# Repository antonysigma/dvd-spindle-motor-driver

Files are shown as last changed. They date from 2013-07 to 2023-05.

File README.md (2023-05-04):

# Spinning flow-cell controller with conventional DVD/BD drives

The custom PID controller board to maintain the rotation speed of the DVD/BD
drive at a user-provided RPM value.

Note: This project is inspired by the blog post
http://akashkumar4u.blogspot.hk/2013/05/cddvd-motor-driver-hack-to-run-its-own.html

Technical specifications:

* Input power: 5VDC, 200mA;

* Output: torque control signal for the DVD spindle motor driver IC, [Rohm BD7998EFS](datasheet/bd7956fs.djvu).

* RPM speed sensing: rotary encoder pulse signal, converted from the built-in hall sensor of the DVD drive.

* Display: kilo-RPM value on the 7-segment LED numerical display;

* MCU Programming interface: SPI bus to program the ATTiny MCU.

* Set point control: Manual adjustment knobs; one for coarse adjustment (+/- 1
  kilo-RPM); one for fine adjustment (+/- 50 RPM).

## Why I made my own board

The board is part of the rotational digital histology imaging system: to study how one can rapidly image a custom Petri dish with adherent mammalian cells. The disk/dish is scanned with a one-dimensional image sensor (at 100 MHz line rate) following a outward spiral trajectory, so it is absolutely necessary to control the RPM precisely for image registration.

Reference: Anson H. L. Tang, P. Yeung, Godfrey C. F. Chan, Barbara P. Chan, Kenneth K. Y. Wong, and Kevin K. Tsia, “Time-stretch microscopy on a DVD for high-throughput imaging cell-based assay,” Biomed. Opt. Express 8, 640–652 (2017). https://doi.org/10.1364/BOE.8.000640

The schematic is eventually re-designed to synchronize the RPM with the x-axis linear stage.

## Preview

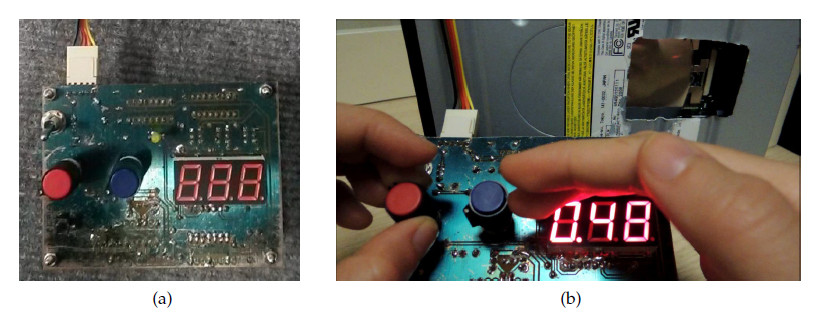
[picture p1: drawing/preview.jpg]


## Schematics

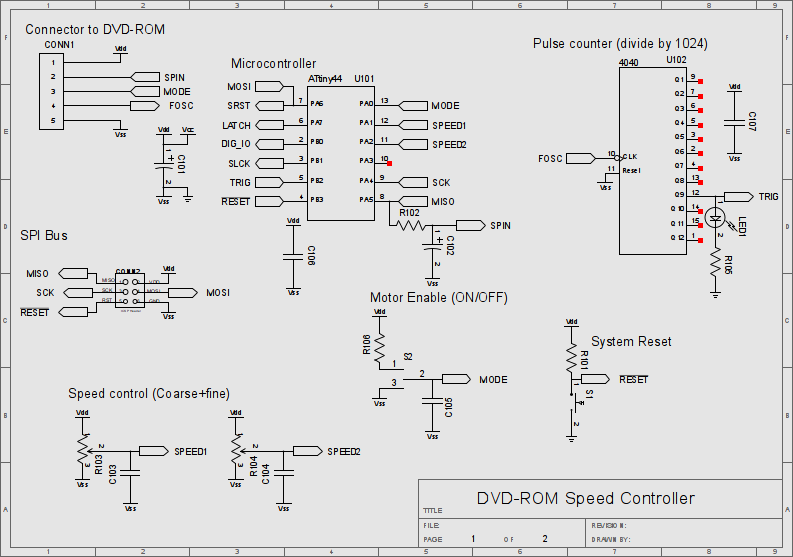
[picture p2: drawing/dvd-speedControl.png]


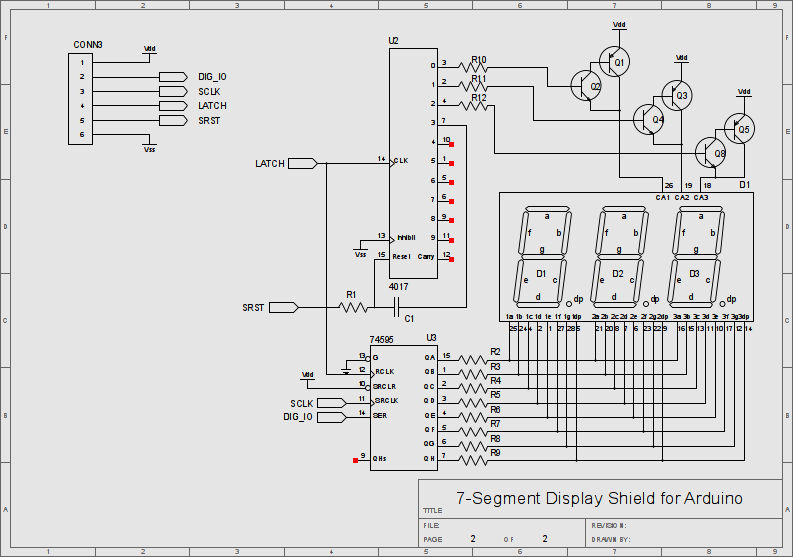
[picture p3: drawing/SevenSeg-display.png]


## Design intent

The overarching goal, at the time, was to justify the investment of custom control circuit in an optics research lab. With minimal budget, I wish to prove that:

* it is intuitive enough to reverse-engineer a conventional DVD drive for manual RPM control;

* advanced control logic, e.g. lead-lag compensation, can be programmed with MCUs; no hardwired analog OpAmp circuit required.

* the RPM control board and the DVD drive can be quickly integrated into the high-speed microscopy system (at 100 image line scan rate) without impacting research timeline.

... so I can justify more inventment on a professionally made driver board for the research, like what [Ultima Genomics did with their spinning flowcells](https://www.biorxiv.org/content/10.1101/2022.05.29.493900v1.full).

**Understanding the DVD motor spindle driver IC** The DVD drive is dissembled to
inspect spindle motor driver IC (Fig. 1a) on the control board. The
corresponding datasheet is sought from the Internet to locate the essential pin
to interface with the motor control functions (Fig. 1b). Specifically, pin 35,34
toggles between spindle motor enable and DVD tray enable; pin 26 controls the
spindle motor torque; pin 43 relays the speed information back to the
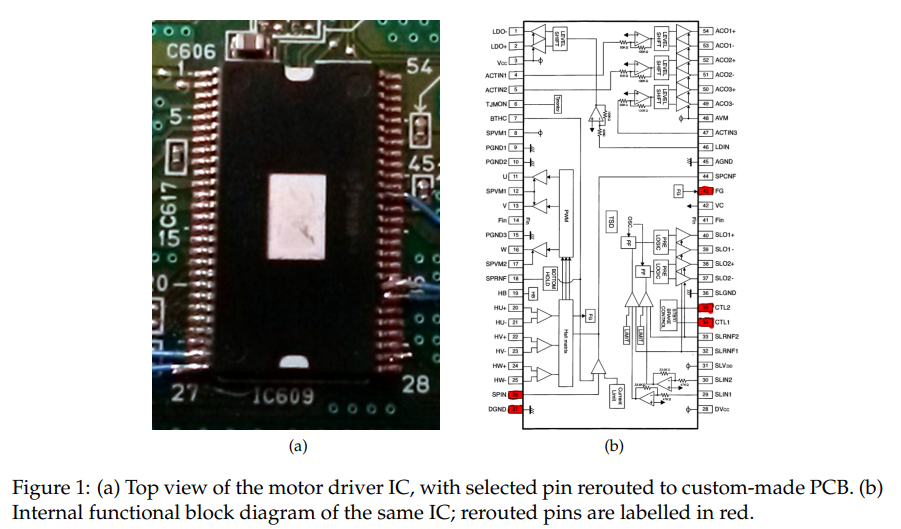
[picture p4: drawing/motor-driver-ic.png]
microcontroller (Fig. 1). 

**Developing the feedback control theory**

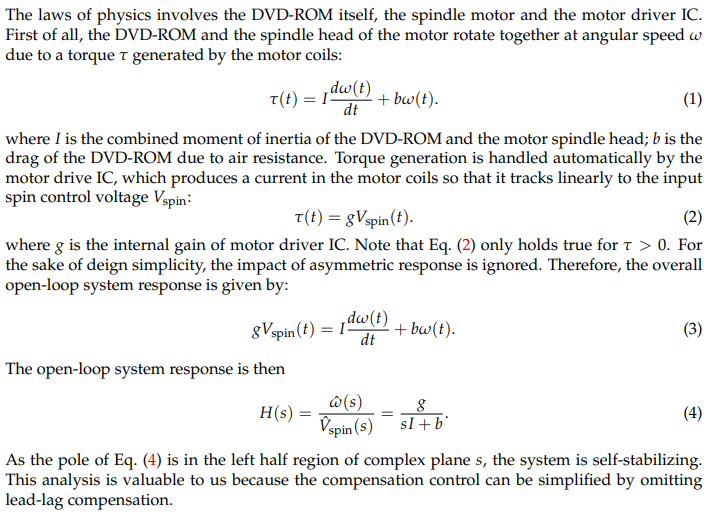
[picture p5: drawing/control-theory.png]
control theory

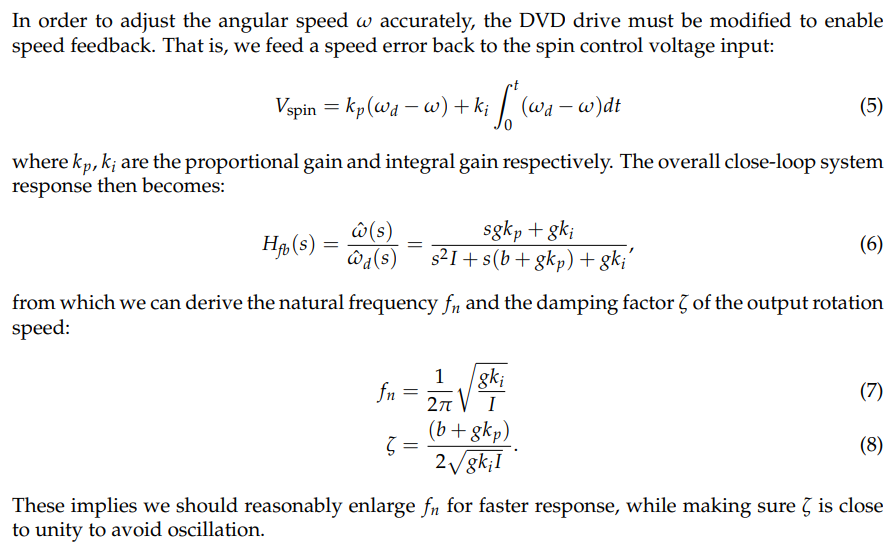
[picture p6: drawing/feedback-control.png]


**Decoding the rotary encoder signal**

The same DVD spindle motor IC also decodes the built in Hall sensor to return
the 3 phase quadrature signal at TTL. For the quick prototyping purpose, we do
not need to tell the absolute position or the spin direction of the disk, so we
only pick one signal out of the 3 phase bus to measure speed.

We offload pulse conuting logic to an external IC (74HC4040) to reduce the pulse
rate by 1024 times. Otherwise, the MCU running at 8MHz will be overwhelmed by
the edge interrupt. The RPM measurement is implemented in the MCU, we the time
interval between adjacent edge interrupt is estimated from the 8MHz MCU clock.

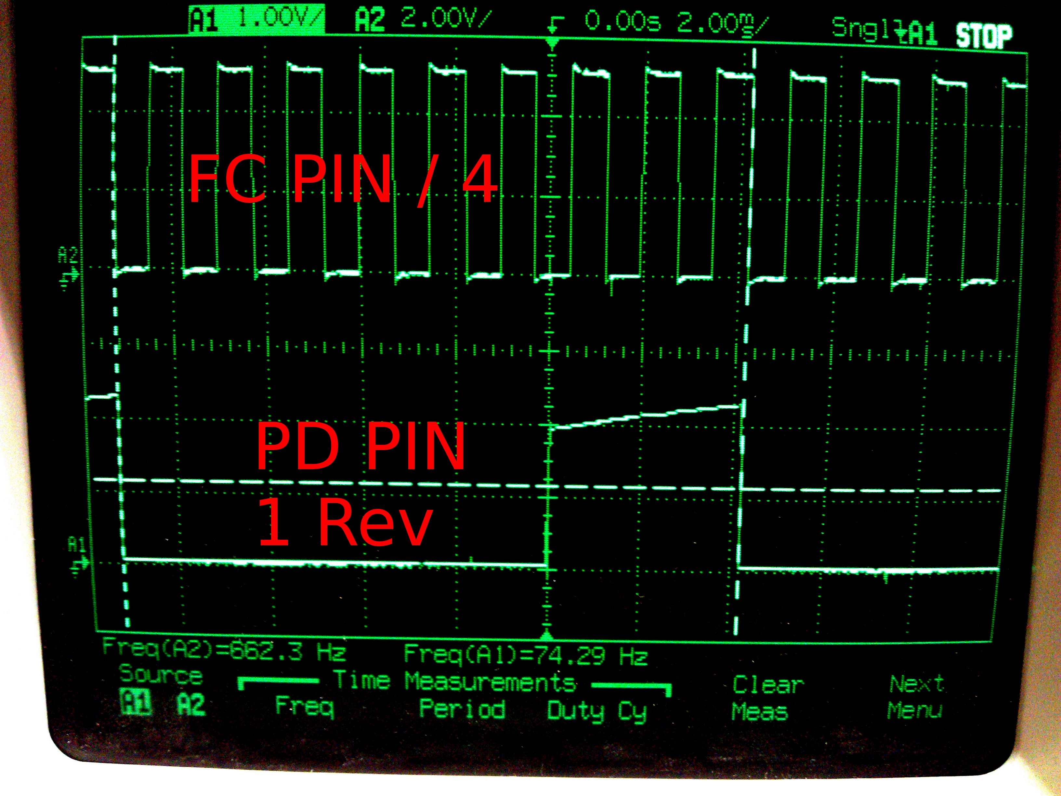
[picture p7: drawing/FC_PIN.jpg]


## PCB routing

The board was designed at the time when solder paste and cheap PCB fabhouse were cost prohibitive. We developed the photo-resist mask, and etch the PCB in house.
Through hole component were the only options. To create throughhole vias, a solid core copper at 22 AWG were inserted and buried with solder.

If I were to route the PCB again, I would have used SMT components to shrink the board down.

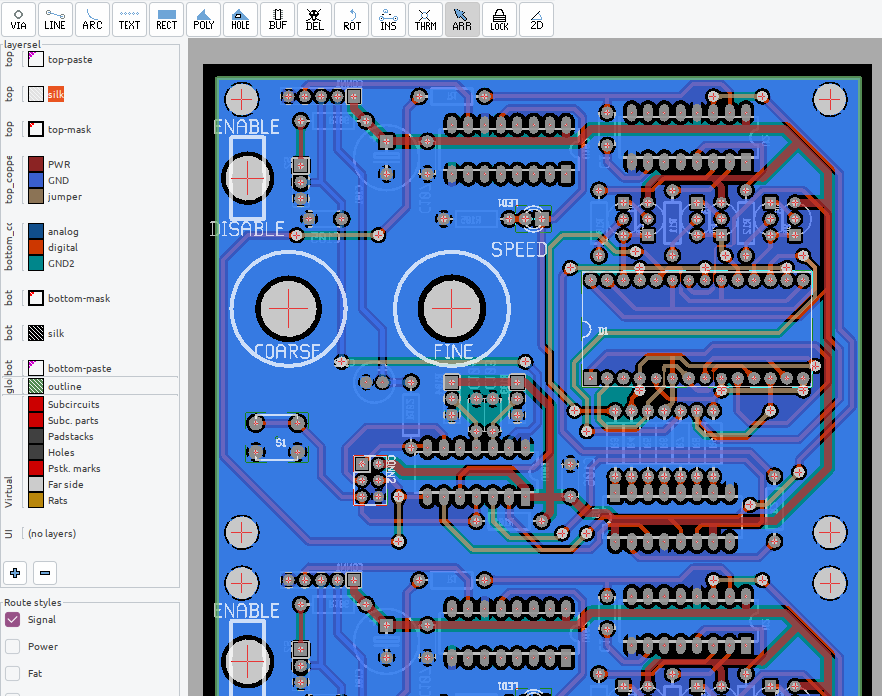
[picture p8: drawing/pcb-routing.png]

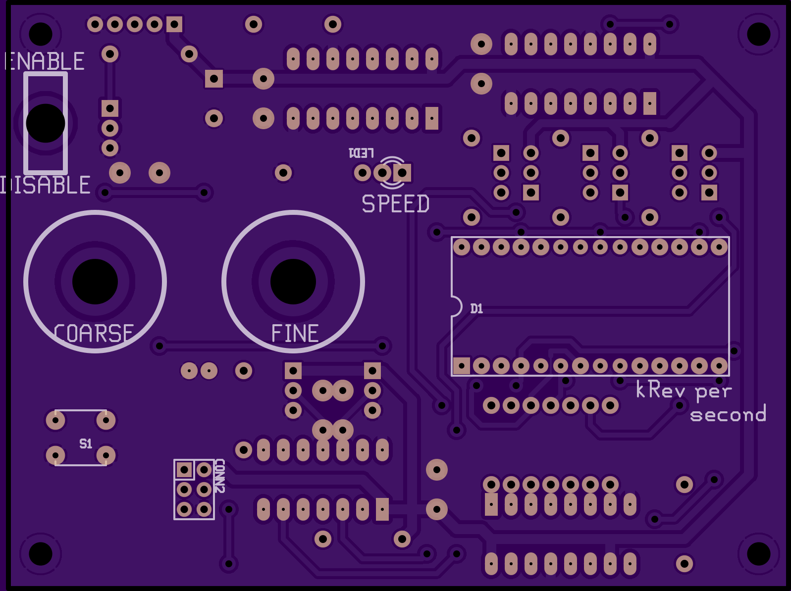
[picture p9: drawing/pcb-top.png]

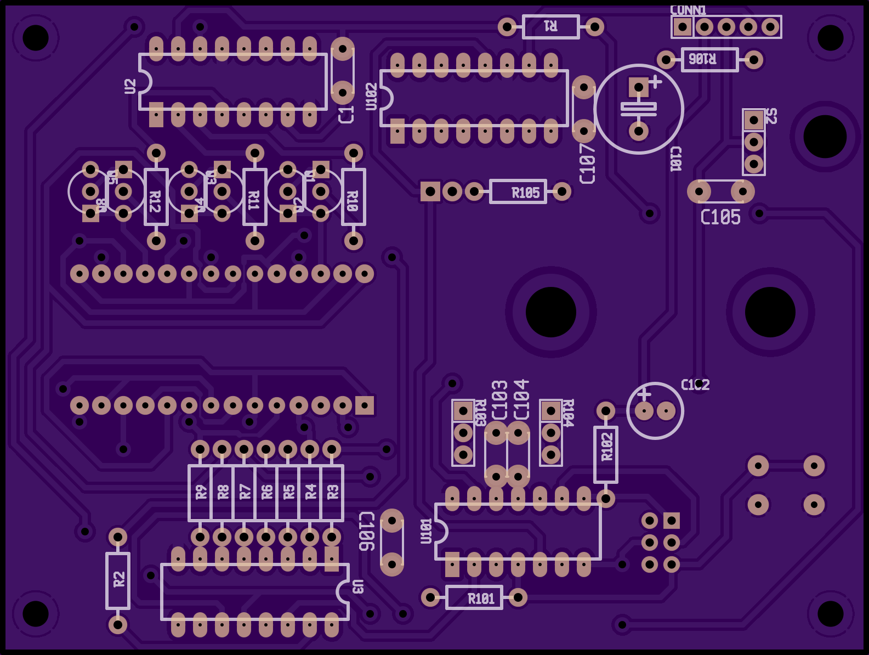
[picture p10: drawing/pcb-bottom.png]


## Literatures

* DVD motor driver hack to run its own 3 phase BLDC motor. http://akashkumar4u.blogspot.hk/2013/05/cddvd-motor-driver-hack-to-run-its-own.html

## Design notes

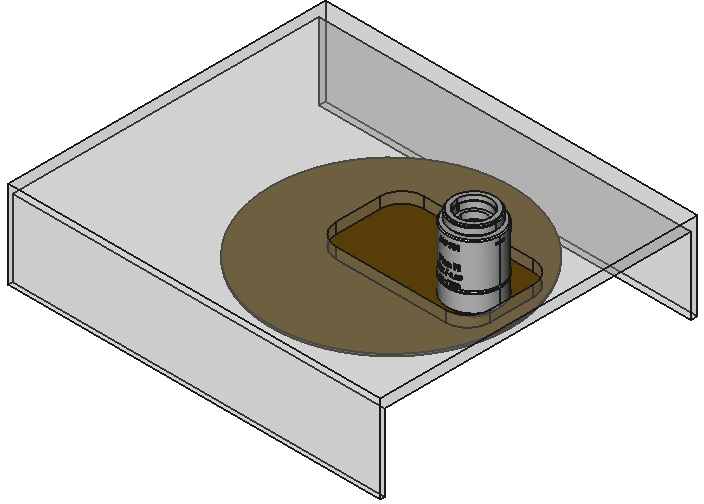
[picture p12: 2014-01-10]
drawing/DVD-hole.png

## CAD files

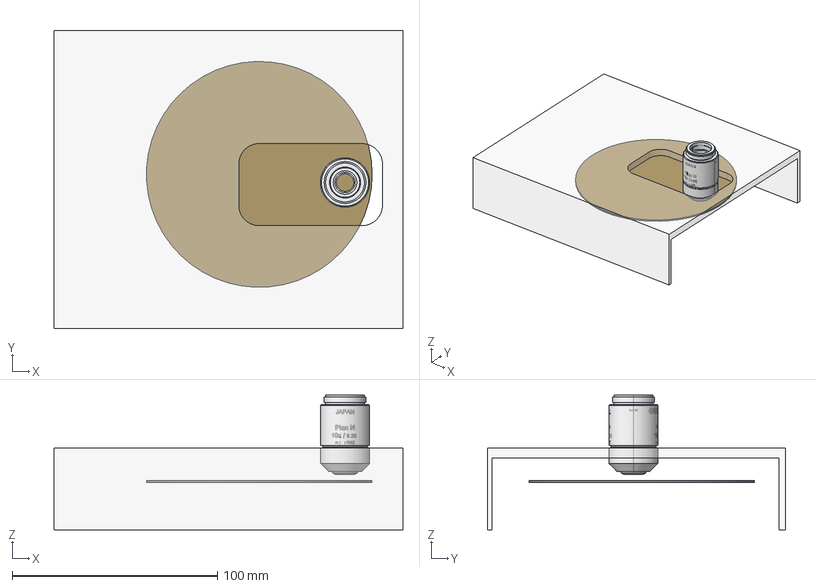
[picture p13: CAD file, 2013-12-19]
drawing/DVD-hole.fcstd
170.0 x 145.0 x 65.7 mm
Case
Objective
DVD-ROM

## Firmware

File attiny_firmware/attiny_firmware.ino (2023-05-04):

//**************************************************************//
//  Name    : shiftOutCode, Hello World
//  Author  : Carlyn Maw,Tom Igoe, David A. Mellis
//  Date    : 25 Oct, 2006
//  Modified: 23 Mar 2010
//  Version : 2.0
//  Notes   : Code for using a 74HC595 Shift Register           //
//          : to count from 0 to 255
//****************************************************************
#include "PIDcontrol.h"
#include "sevenSeg.h"

/******************************************************************************/
long deltaT = 1000;

long timePast = millis();
void
measureSpin() {
    // static long timePast = millis();
    long timeNow = millis();

    deltaT = timeNow - timePast;
    timePast = timeNow;

    // Update kilo-revolution per minute =
    // (128 / dT) / (18 Ticks / Rev)
    //        * (60k millisecond / 1 minute) * (1 kiloRev / 1000 Rev)
    // dT = millisecond / tick
    float kilo_rev = 1280. / (deltaT * 3);
    convert2Digits(kilo_rev);
}

/******************************************************************************/
void
setup() {
    // set pins to output so you can control the shift register
    pinMode(latchPin, OUTPUT);
    pinMode(clockPin, OUTPUT);
    pinMode(dataPin, OUTPUT);
    pinMode(resetPin, OUTPUT);

    // pinMode(spinPin, OUTPUT);
    // pinMode(speedPin, INPUT);

    // Reset the Display
    DisplayReset();

    // Counter based on external input (On pin B2)
    attachInterrupt(0, measureSpin, RISING);

    // Set torque output (default brake)
    analogWrite(spinPin, 0);
}

long timePID_Past = millis();
void
loop() {
    // static long timePast=millis();
    long timeNow = millis();

    if (timeNow - timePID_Past > sampleT) {
        PID_control(deltaT);
        timePID_Past = timeNow;
    }
    DisplayDigits();
}

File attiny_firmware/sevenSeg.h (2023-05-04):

#ifndef __sevenSeg_H_
#define __sevenSeg_H_

// include types & constants of Wiring core API
#include "WConstants.h"
#include "core_pins.h"

// Pin connected to ST_CP of 74HC595
const int latchPin = PIN_A7;
// Pin connected to SH_CP of 74HC595
const int clockPin = PIN_B1;
////Pin connected to DS of 74HC595
const int dataPin = PIN_B0;
/// Digit reset pin
const int resetPin = PIN_A6;

void DisplayReset();
void convert2Digits(float num);
void DisplayDigits();

#endif

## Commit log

2013-07-11 First working circuit plus firmware
    [SevenSeg-display.sch, dvd-speedControl.sch]
2013-07-12 Placing the components on the PCB
    [SevenSeg-display.sch, dvd-speedControl.sch]
2013-07-13 Placed all components onto PCB board
    [dvd-speedControl.sch]
2013-07-15 Completed all but routes to display board connector
2013-07-16 Add limiting resistor to mode switching input
    [dvd-speedControl.sch]
2013-07-16 Fixed all Design rules except drill size and clearance of screw holes.
2013-07-16 Put resistor R106 to the far side
2013-07-16 Add ground plane on the bottom side; Fix orientation of resistor R106
2013-07-19 Increase pad size of the 7-Segment board
2013-07-24 Changed C102 to polar footprint; increase pad diameter of led; Move toggle switch further away from other components
    [dvd-speedControl.sch]
2013-07-24 Put Capacitor C102 to the other side
2013-07-26 Re-add separate libraries of arduino code
2013-07-30 Convert board to metric scale (100x75mm)
2013-07-30 Move traces away from the edge to fit smaller board
2013-08-02 Use Pin A2 to accept speed information
2013-08-02 Finalized dual panel PCB
2013-08-07 Attempt to calibrate measured speed
2013-08-07 Calibrate RPM; use floating point in PID control
2013-08-08 Attempt to calibrate PI gain to match commit cf918cfb
2013-11-15 Improve sensitivity of the fine adjustment pin
2013-11-15 FC Pin calibration
2013-12-17 Edit PCB silkscreen
2013-12-19 PCB preview
2013-12-19 Hole cutting
    [DVD-hole.fcstd]
2015-01-23 Edit firmware to reflect change to clock prescaler
    [dvd-speedControl.sch]
2023-05-04 Organize contents in sub-directories
    [SevenSeg-display.sch, dvd-speedControl.sch]
